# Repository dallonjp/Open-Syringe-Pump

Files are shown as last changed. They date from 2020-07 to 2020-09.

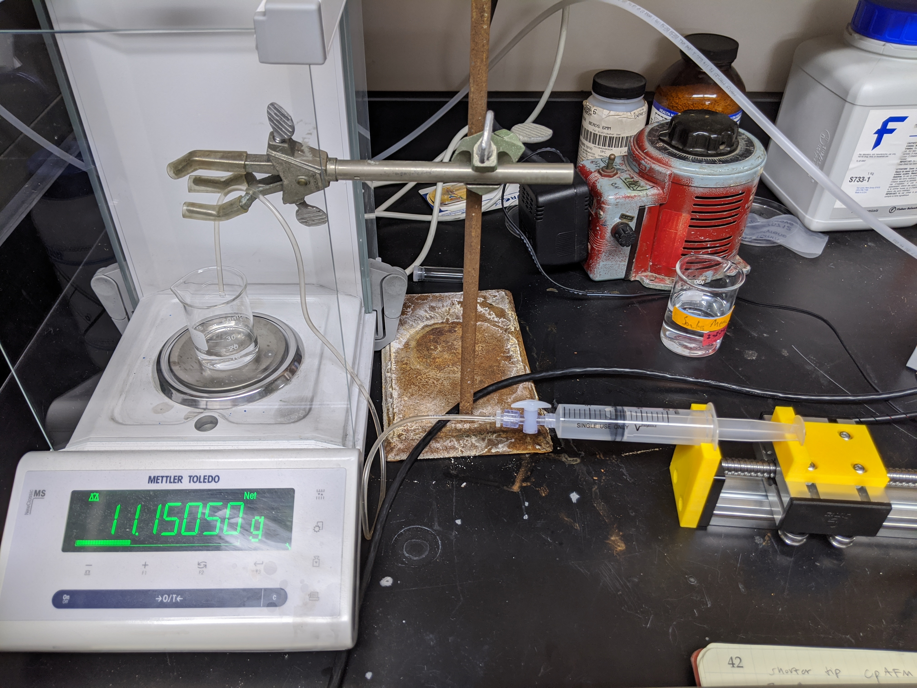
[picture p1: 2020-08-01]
Pictures/IMG_20200718_154940 (1).jpg

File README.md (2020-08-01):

# Open-Syringe-Pump
A simple open source syringe pump using readily available and 3D printed parts.
Included is a windows application for interfacing with the pump as well as the arduino code that interfaces with the application.


## Please read the Instructions folder to detailed build instructions
If something is missing, feel free to message me on Discord: dallonjp#9497

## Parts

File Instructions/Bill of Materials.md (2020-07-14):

# Bill of Materials
* Arduino of choice (This build uses the arduino nano v3)
* Ball screw linear actuator
  * 100mm Travel Length Linear Stage Actuator DIY CNC Router Parts X Y Z Linear Rail Guide Sfu1402 Nema17 by MySweety
  * https://www.amazon.com/dp/B01L6W1GRG/ref=cm_sw_em_r_mt_dp_U_Qs5-Eb7S7W0HF
  * If this is no longer being manufactured, another one with a Nema 17 stepper motor will work. You will need to adjust the 3D printed parts accordingly.
* Polulu A4988 stepper driver
  * https://www.pololu.com/product/1182
* 50-100 uF capacitor
* USB cable to connect to arduino
* 12 V power supply
* Limit switch end stop
  * https://www.amazon.com/dp/B06XTB7WMK/ref=cm_sw_r_tw_dp_x_8F5-EbGETP0D2
* 3D printed parts (see .stl folder or the .f3d folder)
* 20 mL Air-Tite glass syringe
  * https://www.amazon.com/Air-Tite-Glass-Syringe-Metal-Clear/dp/B00BQLLMQ8/ref=cm_cr_arp_d_pb_opt?ie=UTF8
* 4 M5 screws
* 2 M2 screws
* Insulated 8/10/12 gauge wires
* Molex pin set

# Tools required
* Molex pin crimping tool
* Soldering iron and solder
* Wire strippers/pliers
* Access to a 3D printer
* Metric hex wrenches
* Multimeter
* Small philip's screwdriver

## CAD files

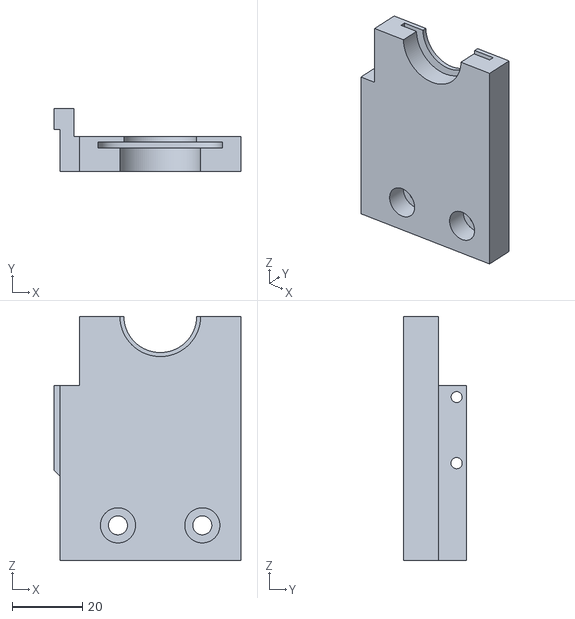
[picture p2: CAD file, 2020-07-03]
Instructions/stl files/20 mL Syringe/syringe_tube_holder.stl
53.2 x 18.0 x 69.4

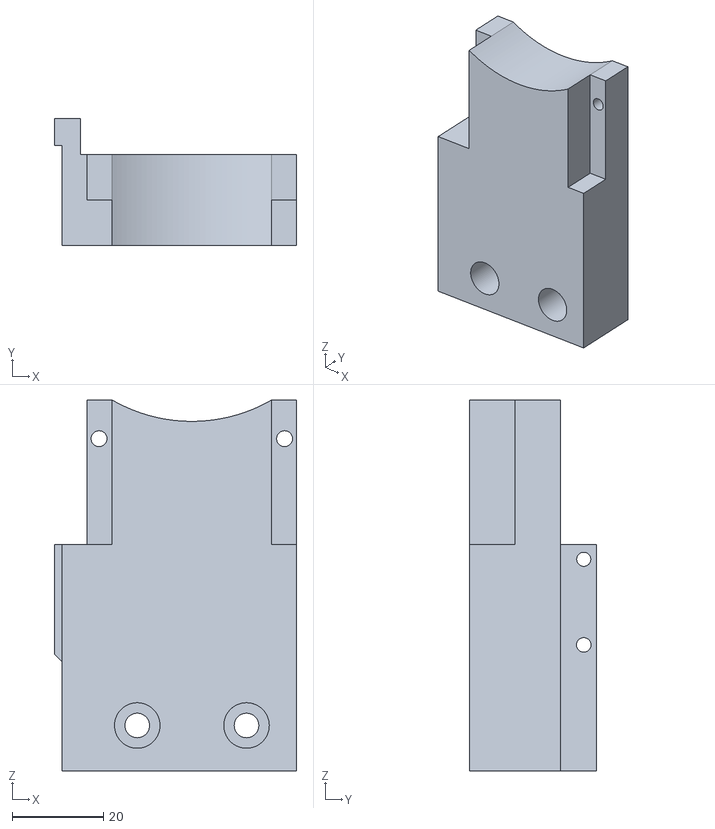
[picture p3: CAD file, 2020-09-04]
Instructions/stl files/universal syringe/syringe_holder.stl
53.2 x 28.0 x 81.5

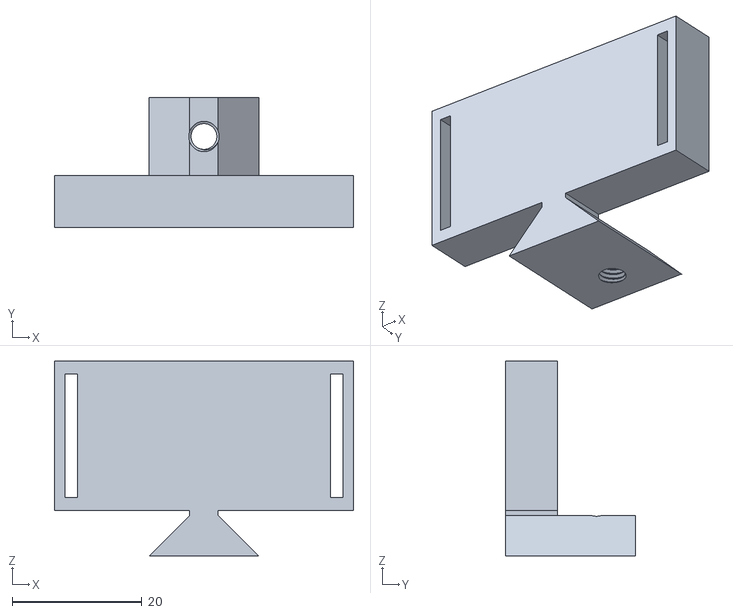
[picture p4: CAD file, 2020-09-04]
Instructions/stl files/universal syringe/plunger_holder.stl
46.0 x 20.0 x 30.0

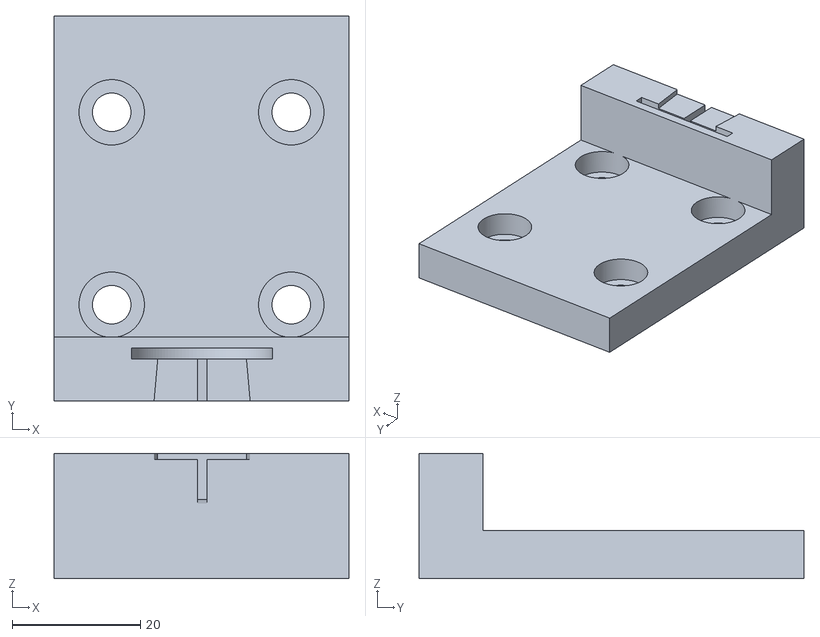
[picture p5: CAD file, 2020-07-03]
Instructions/stl files/20 mL Syringe/syringe_plunger_holder.stl
46.0 x 60.0 x 19.5

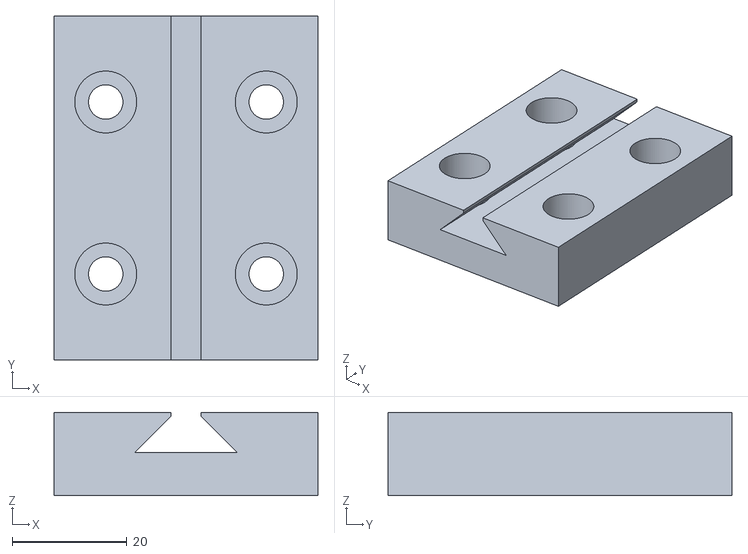
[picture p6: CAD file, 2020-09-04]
Instructions/stl files/universal syringe/holder_base.stl
46.0 x 60.0 x 14.5

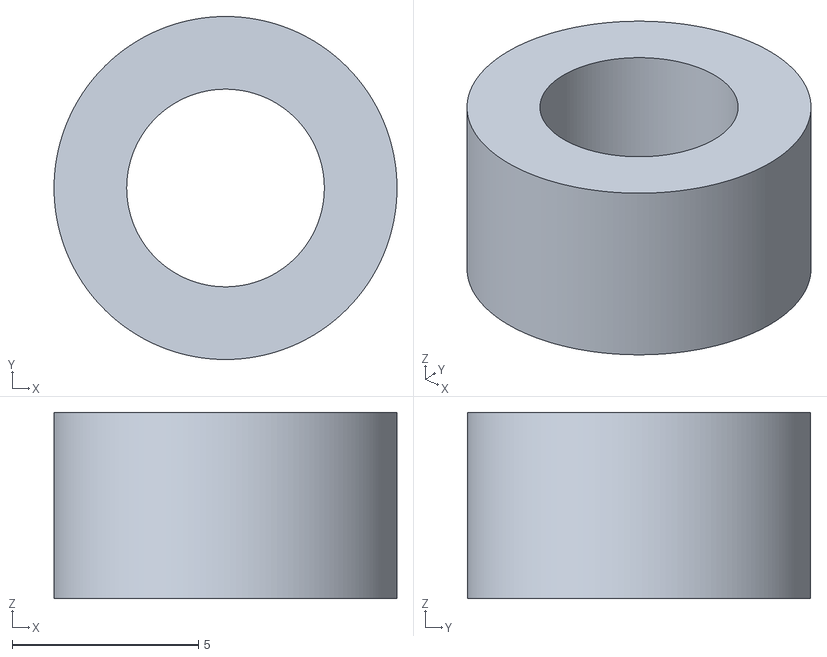
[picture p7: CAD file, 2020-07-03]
Instructions/stl files/20 mL Syringe/screw_hole_filler.stl
9.20 x 9.20 x 4.99

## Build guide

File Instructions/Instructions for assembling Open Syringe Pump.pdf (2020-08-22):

Instructions for assembling and operating Open Syringe Pump

These instructions assume all the parts have been printed/acquired, and the linear actuator (see Amazon link in Bill of Materials), fasteners, and tools are also in hand.

The Syringe Pump

1. Steel plates
a. Cut a piece of hardened steel shim (<= 3 mm thick) to two rectangles.
b. Using the 3D printed “syringe_holder.stl” piece, mark on each steel plate where the holes should be drilled by sliding a drill bit into the holes through the opposite side. (Note: the top of the steel plates should not be above the lower edge of the concave portion of the syringe holder while marking the holes)
c. Drill the marked holes using an M3 or 1/8” drill bit.
2. Plunger holder assembly
a. Attach one of the steel plates to the “plunger_holder.stl” printed part.

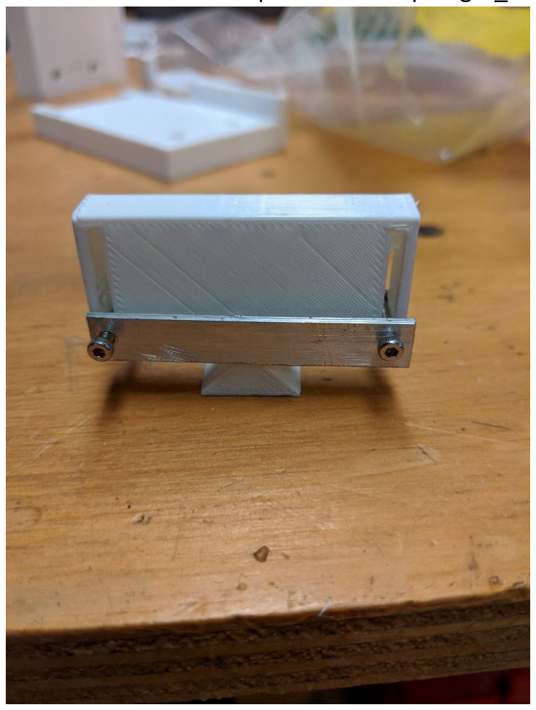
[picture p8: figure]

b. Insert an M5 set screw into the “plunger_holder.stl”. (Do not tighten)

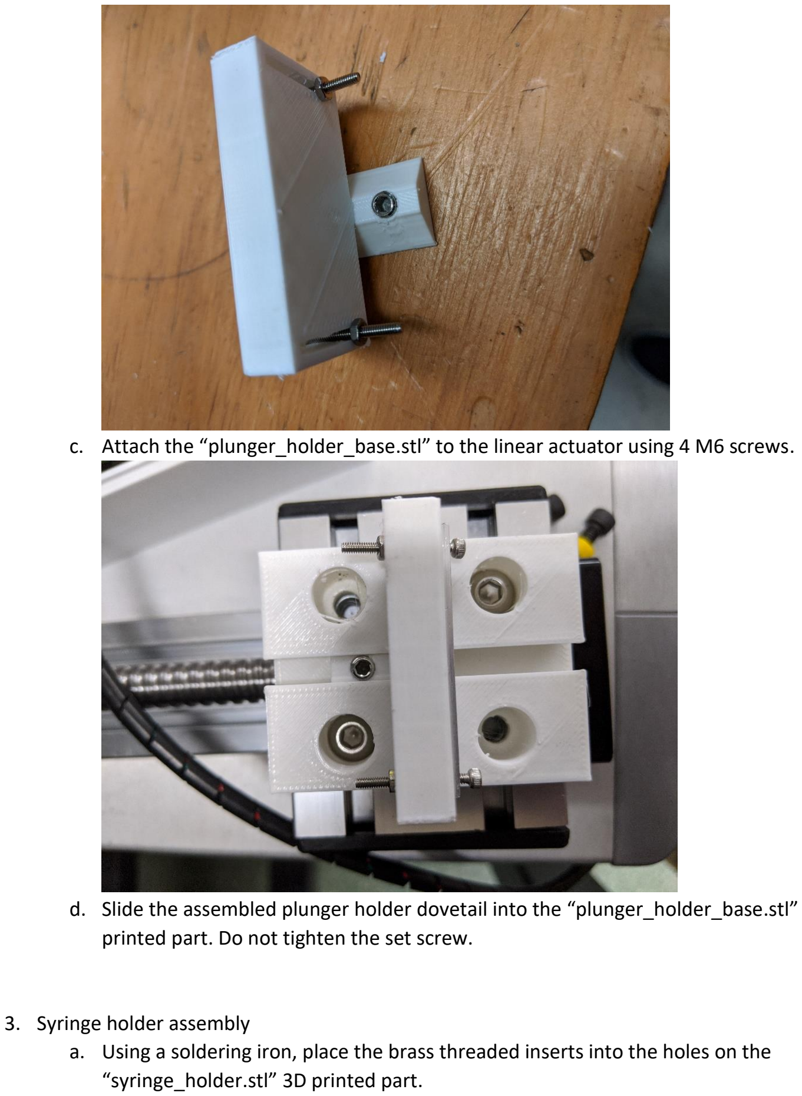
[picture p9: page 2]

c. Attach the “plunger_holder_base.stl” to the linear actuator using 4 M6 screws.
d. Slide the assembled plunger holder dovetail into the “plunger_holder_base.stl” printed part. Do not tighten the set screw.
3. Syringe holder assembly
a. Using a soldering iron, place the brass threaded inserts into the holes on the “syringe_holder.stl” 3D printed part.

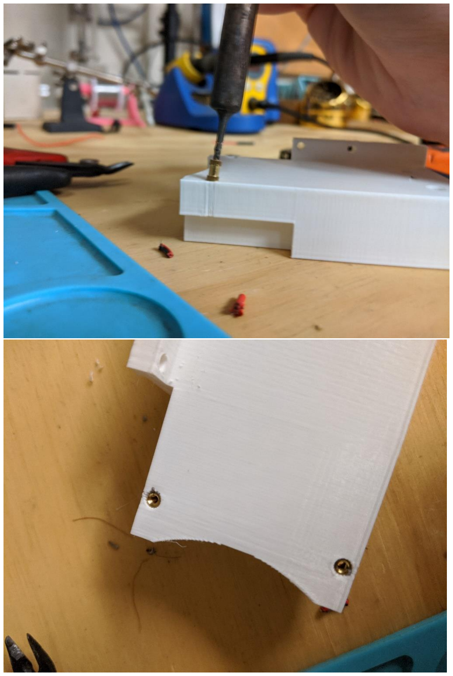
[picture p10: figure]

b. Attach the other steel plate to the back side of the “syringe_holder.stl” using 2 M2 screws. Using 2 M3 screws, attach the mechanical endstop to the base of the “syringe_holder.stl”.

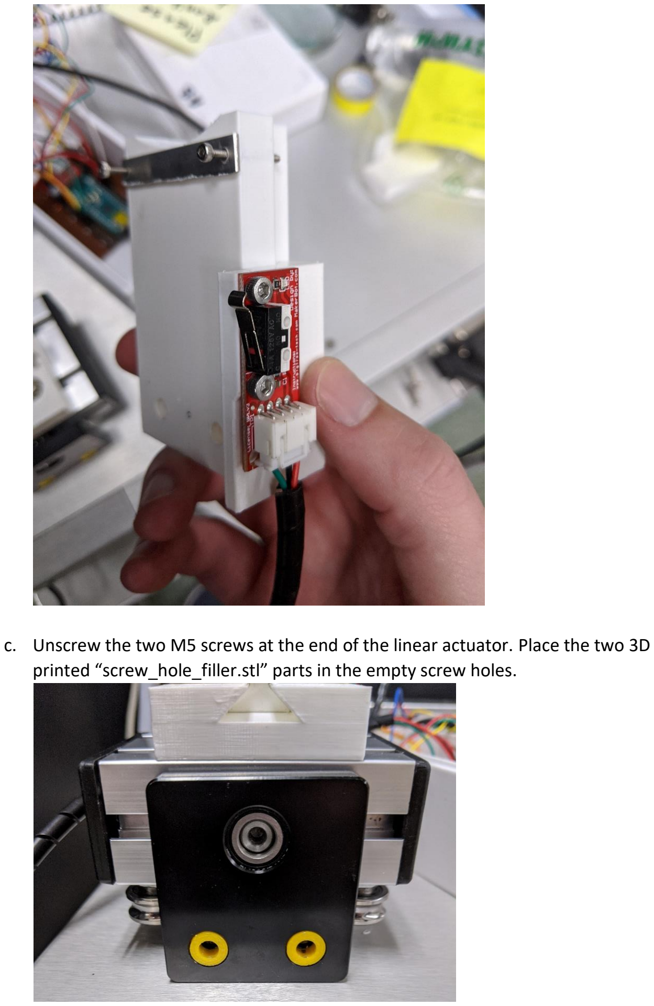
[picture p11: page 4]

c. Unscrew the two M5 screws at the end of the linear actuator. Place the two 3D printed “screw_hole_filler.stl” parts in the empty screw holes.

d. Attach the assembled syringe holder using the two M5 screws from the linear actuator to secure it in place.

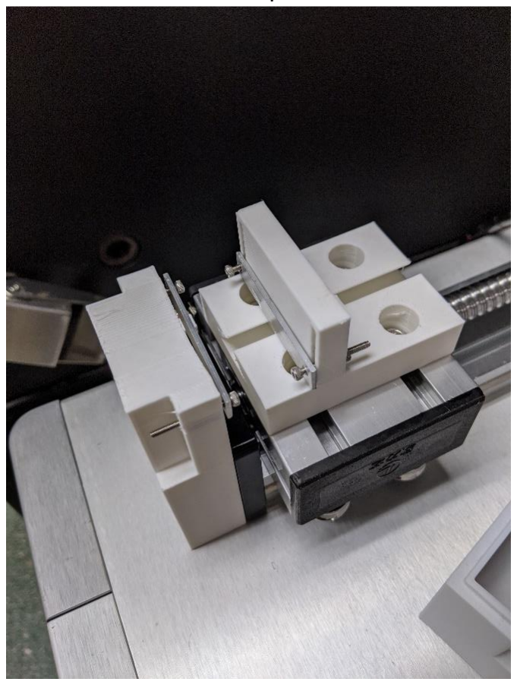
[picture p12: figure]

The Microcontroller

1. Refer to the wiring diagram below to wire the microcontroller hardware.

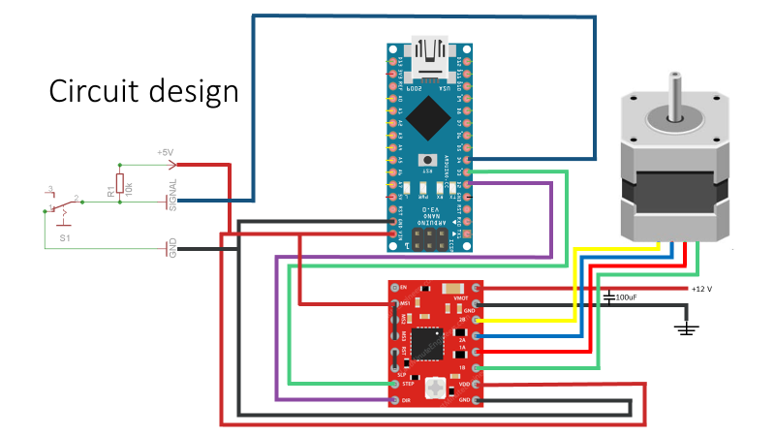
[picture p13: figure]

2. Using either screw terminals or solder, attach the 12 V power source and ground cables from the 12 V power supply to the VMOT and GND pins of the A4988 board. (note: the only way to power off the system is to unplug the power supply)
3. The 40-100 μF capacitor is in parallel with the 12V and ground in order to help protect the board.
4. Note: the A4988 driver is configured in the circuit to have 1/16 steps instead of the full steps. (The MS1, MS2, and MS3 pins are all connected)
5. Connect the Arduino d2 pin to the DIR pin on the A4988 driver, and the d3 pin to the STEP pin on the driver.
6. Connect the Arduino 5V pin to the MS1/MS2/MS3 pins on the driver.
7. Connect the RST and SLP pins on the driver.
8. Connect the Arduino 5V pin to the VDD pin on the driver.
9. Connect the Arduino GND pin to the GND pin on the driver.
10. Wire the endstop NC wire (green) to the d3 pin on the Arduino and the NO and ground to the 5V and GND pins on the Arduino, respectively.

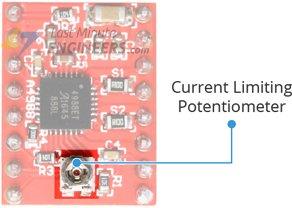
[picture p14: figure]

11. Using a multimeter and a small screwdriver, adjust the current limiting potentiometer on the driver so that the voltage read between the potentiometer and the GND pin is about 0.6 V. Follow this guide: https://ardufocus.com/howto/a4988-motor-current-tuning/ .
12. Connect the Nema 17 stepper wires to the 2B, 2A, 1B, 1A pins on the driver as shown in the diagram. If a different stepper motor is used than the one that comes with the actuator on Amazon, you will need to wire it according to that motor’s specifications.
13. If when running the motor is loud/jumpy, adjust the potentiometer to reduce the reference voltage.

Software: Arduino Sketch

1. Download the Arduino IDE from the Microsoft store: https://www.microsoft.com/en-us/p/arduino-ide/9nblggh4rsd8?activetab=pivot:overviewtab (https://www.microsoft.com/en-us/p/arduino-ide/9nblggh4rsd8?activetab=pivot:overviewtab)
2. Load the sketch from the Github repository in the IDE environment.
3. Select the board “Arduino Nano” under the Tools tab.
4. Plug the Arduino into a USB port on the computer.
5. Select the appropriate COM port under the Tools tab.
6. Click the “Upload” button at the top of the page.
7. The Arduino LEDs should flash while the sketch is uploaded.
8. Keep the Arduino connected to the computer.

Software: Windows Application

1. Download the executable file.
2. Run the executable file.
3. Click “Settings” and select the COM port for the Arduino that is plugged into the machine.

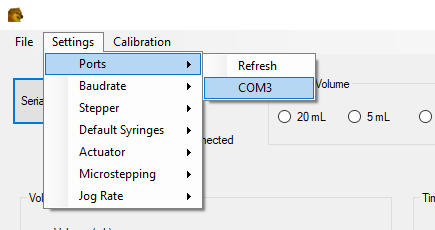
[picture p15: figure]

4. Click the “Serial Connect” button.

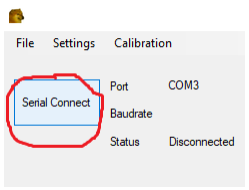
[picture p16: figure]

5. If the Arduino does not connect, try clicking the “Serial Connect” button again, or try a different COM port.
6. The status will show “Connected” if the Arduino is connected to the application.
7. Once connected, zero the position of the stepper by clicking the “Zero Position” button. (note: there should not be a syringe attached during this step)

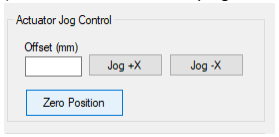
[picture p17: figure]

8. Attaching the syringe:
a. Use the screws on the syringe_holder.stl part to grip the syringe flanges.

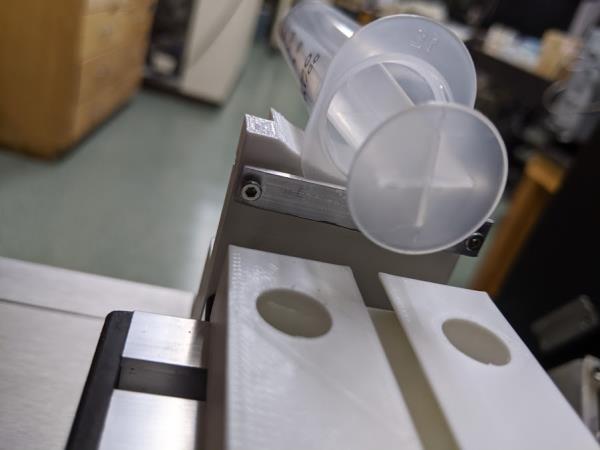
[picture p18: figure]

b. Pull the syringe plunger out to make it easier to attach the plunger holder.

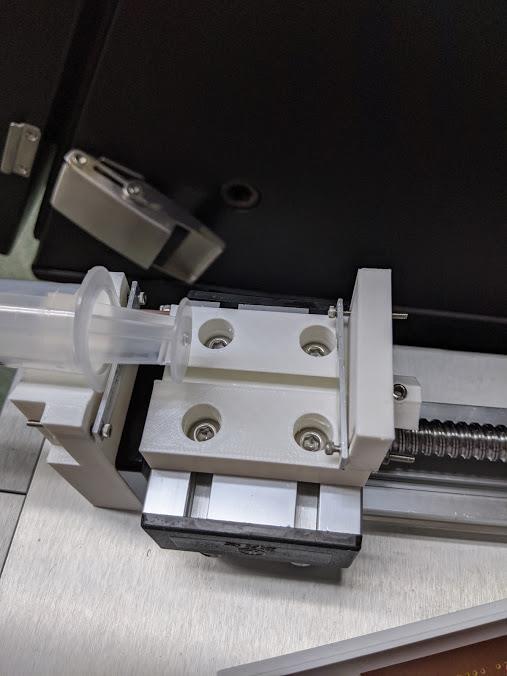
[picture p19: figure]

c. Attach the plunger to the plunger holder with the screws and steel plate.

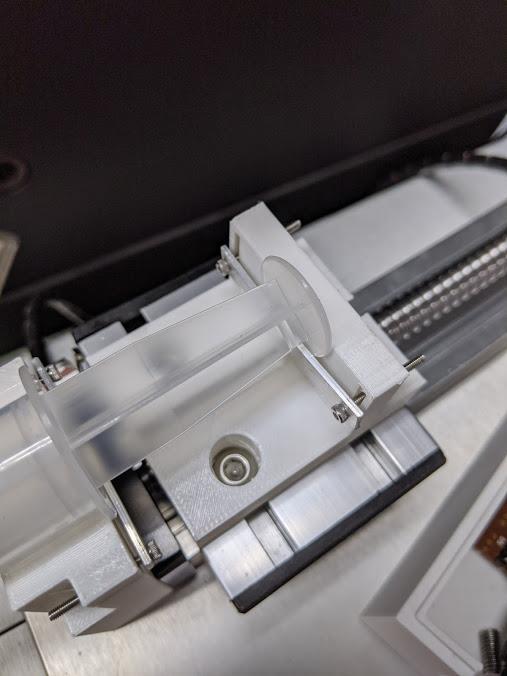
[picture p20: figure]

d. Push the plunger and syringe holder all the way so that there is zero volume in the syringe.
e. Secure the plunger holder in place by tightening the set screw.

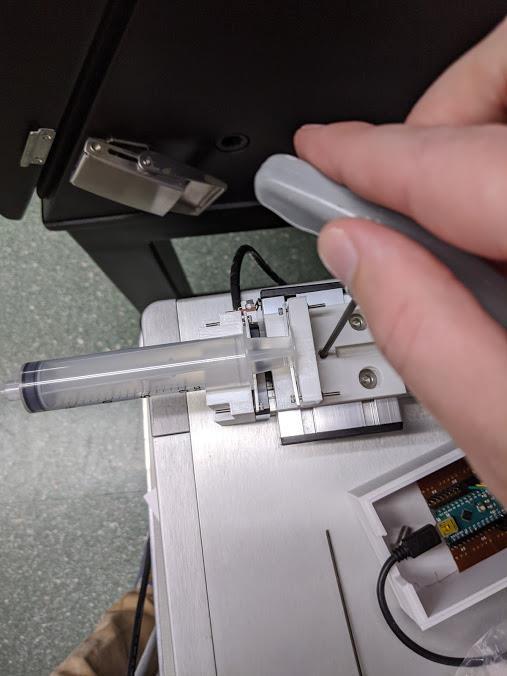
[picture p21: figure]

9. Make sure the syringe volume is selected in the application. (Note: the default syringe volumes can be changed in the settings).

Syringe Calibration

1. Once the position is zeroed, a syringe is attached, and the correct volume selected, begin by aspirating a known volume of fluid, which can be anything less than or equal to the syringe volume. Typically, you should aspirate the entire syringe volume in order to make the calibration more accurate.
a. Make sure the syringe is leading into whatever fluid you are aspirating.
b. Type in the volume in the “Volume (mL)” textbox.

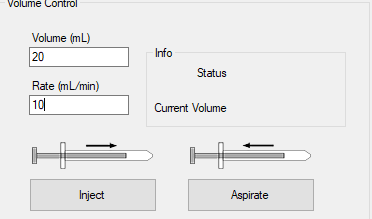
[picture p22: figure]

c. Set a rate in the “Rate (mL/min)” textbox (usually 10/20 mL/min).

d. Click the “Aspirate” button and wait for the Arduino to finish the operation.
2. Set a theoretical injection volume, for example you could set it at 0.5 mL.
3. Next, set up a beaker/container in an analytical balance with the syringe being able to inject directly into the container. Zero the weight of the container.

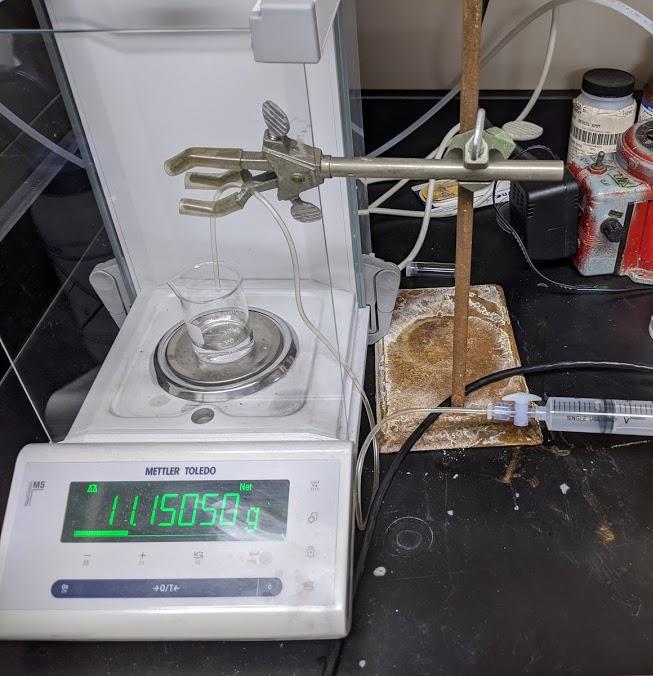
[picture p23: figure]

4. Using the windows application, inject your theoretical volume repeatedly and record the weight until the syringe is empty or the volume remaining is less than the theoretical volume.
a. Type in the theoretical volume in the “Volume (mL)” textbox.
b. Set a rate in the “Rate (mL/min)” textbox. (Rate has little effect on calibration)
c. Click the “Inject” button.
5. Use the current temperature, pressure, and density of the fluid to calculate the volumes of each actual injection.
6. Average the actual injection volumes.
7. Under the “Calibration” tab, click the volume of syringe that you are calibrating.
8. Enter the average actual measured volume and the theoretical delivered volume into the appropriate fields and click “Okay”.

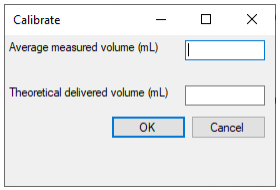
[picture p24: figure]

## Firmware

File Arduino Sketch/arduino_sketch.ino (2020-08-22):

#include <AccelStepper.h>
#include <FlexiTimer2.h>
#define dirPin 2 //digital pin 2 on arduino connects to dir pin on A4988
#define stepPin 3 //digital pin 3 on arduino connects to step pin on A4988
#define homeButton 5 //digital pin 5 on arduino connects to normally closed (green) wire on endstop
#define motorInterfaceType 1

long steps;
long init_homing=-1;
long stepto;
long mspeed;
long maccel;
long mdir;
long mpos;
long interval;
long elapsed=0;
long defaultrate;
long defaultaccel;
long timenow;
long timethen;

int msg_length;
bool connected =false;
bool datarvd = false;
char  userInput[20]; 
char userInput2[6];

// Create a new instance of the AccelStepper class:
AccelStepper stepper = AccelStepper(motorInterfaceType, stepPin, dirPin);

void setup()
{  
    //set up serial connection
    Serial.begin(9600);
    Serial.setTimeout(1000); 
    pinMode(dirPin,OUTPUT);
    pinMode(stepPin,OUTPUT);
}
void loop()
{    
    while(Serial.available()>0){
      
      char handshake = Serial.read();
      switch (handshake){
        case 'a':
        //connect to app
          delay(100);
          Serial.println("hello winform");
          delay(100);
          getdefaults();
        break;
        case 'b':
        //home sequence
        homestepper();
        break;
        case 'c':
        //movement
          moveto();
        break;
        case 'e':
        //change acceleration
          changeaccel();
        break;
        case 'f':
        //timed injection
        timedaction();
        break;
        case 'd':
        //stop current operation
        break;

        default:

        break;
      }
    }
}
void timedaction(){
  while (!datarvd){
    if(Serial.readBytes(userInput,20)==20){
      for (int i=1; i<10; i++){
        steps=steps*10+userInput[i]-'0';
      }
      for (int j=11;j<20;j++){
          interval=interval*10+userInput[j]-'0';
        }
      elapsed=0;
      stepto=stepper.currentPosition()-1;
      stepper.setMaxSpeed(10000);
      stepper.setAcceleration(5000);
      while (elapsed<interval){
        if (Serial.available()>0){
          interval=0;
          steps=0;
          break;
        }else{
          delay(steps);
          stepper.moveTo(stepto);  
          stepper.run();
          elapsed=elapsed+steps;
          stepto=stepto-1;
        }
      }
      interval=0;
      steps=0;
      datarvd=true;
    }
  }
  datarvd=false;
}

void moveto(){
  while (!datarvd){
    if (Serial.readBytes(userInput,17)==17){
      for(int i=1; i<8;i++){
        steps=steps*10+userInput[i]-'0';
        }
        for (int j=9;j<15;j++){
          mspeed=mspeed*10+userInput[j]-'0';
        }
        mdir = userInput[16]-'0';      
        if(mdir==1){
          mpos = steps*1;
        }else if (mdir==2){
          mpos = steps*-1;
        }
            stepper.move(mpos);
            stepper.setMaxSpeed(mspeed);
            while(stepper.distanceToGo()!=0){
              stepper.run();
              if (Serial.available()>0){
                break;
              }
            }
        steps=0;
        mspeed=0;
        mdir=0;
        datarvd=true;
    }
  }
  datarvd=false;
}
void homestepper(){
  //home sequence
    init_homing=-1;
    pinMode(homeButton, INPUT_PULLUP);

    delay(5);
    //These speed/acceleration values are for 1/16 step on the A4988 (MS1, MS2, MS3 connected to +5V)
    stepper.setMaxSpeed(3000.0);
    stepper.setAcceleration(3000.0);

    while (digitalRead(homeButton)){
      stepper.moveTo(init_homing);
      init_homing--;
      stepper.run();
     // delay(5);
    }
    stepper.setCurrentPosition(0);
    stepper.setMaxSpeed(3000.0);
    stepper.setAcceleration(3000.0);
    //Serial.print(init_homing);
    init_homing=1;

    while (!digitalRead(homeButton)){
      stepper.moveTo(init_homing);
      stepper.run();
      init_homing++;
    }

    stepper.setCurrentPosition(0);
    Serial.write("yup hom");  
}
void changeaccel(){
  while (!datarvd){
    if (Serial.readBytes(userInput,6)==6){
      for(int i=1; i<7;i++){
        maccel=maccel*10+userInput[i]-'0';
        }
            stepper.setAcceleration(maccel);
        maccel=0;
        datarvd=true;
    }
  }
  datarvd=false;
}
void getdefaults(){
  while (!datarvd){
    if (Serial.readBytes(userInput,20)==20){
      for (int i=1; i<10; i++){
        defaultaccel=defaultaccel*10+userInput[i]-'0';
      }
      for (int j=11;j<20;j++){
        defaultrate=defaultrate*10+userInput[j]-'0';
      }
      stepper.setAcceleration(defaultaccel);
      stepper.setMaxSpeed(defaultrate);
      defaultaccel=0;
      defaultrate=0;
      datarvd=true;
    }
  }
  datarvd=false;
}

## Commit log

2020-06-30 Create Bill of Materials.md
2020-07-01 Rename Bill of Materials.md to Instructions/Bill of Materials.md
2020-07-02 Update Bill of Materials.md
